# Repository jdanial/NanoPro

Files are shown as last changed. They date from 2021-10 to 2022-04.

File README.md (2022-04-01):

# NanoPro
## About
**NanoPro 1.0** is an affordable, high-quality, user-friendly, and do-it-yourself single-molecule microscope for super-resolution imaging.  
  
## Assembly and Operation
**NanoPro 1.0** assembly and operation is described in two parts. Part 1 describes assembly and validation of **NanoPro 1.0** and is published as follows:  

**Danial, JSH, Lam, JYL, Wu, Y, Woolley, M, Dimou, E, Cheetham, MR, Emin, D, and Klenerman, D.**  
Constructing a cost-efficient, high-throughput and high-quality single molecule localization microscope for super resolution imaging.  
_Nature Protocols_, 2022.  
  
Files referred to as supplementary in Part 1 can be found [here](https://github.com/jdanial/NanoPro/tree/main/Supplementary%20Files).
  
Part 2 describes the installation and operation of the **NanoPro 1.0** control software and can be found [here](https://github.com/jdanial/NanoPro/blob/main/Part%202%2C%20NanoPro%201.0%20Operation%20Manual.pdf).  
  
Updates (i.e. variations) to parts 1 and 2 are published at:  
https://github.com/jdanial/NanoPro  
  
## Use and citation
Any data or publications arising from the use of NanoPro 1.0 should cite the following paper:  
  
**Danial, JSH, Lam, JYL, Wu, Y, Woolley, M, Dimou, E, Cheetham, MR, Emin, D, and Klenerman, D.**  
Constructing a cost-efficient, high-throughput and high-quality single molecule localization microscope for super resolution imaging.  
_Nature Protocols_, 2022.

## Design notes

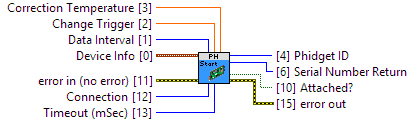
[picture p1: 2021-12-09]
Supplementary Files/Software/Source code/Dependencies/Phidgets/Phidget PH Sensor/Phidget PH Sensor Documentation/PHSensorStartc.png

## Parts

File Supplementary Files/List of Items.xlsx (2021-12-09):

Category | Item number | Description | Catalogue number | Vendor | Quantity | Price Per Item (USD, ex. VAT) | Line Price (USD, ex. VAT) | Order Link | Item Image
Fibre | 1 | 70 µm x 70 µm, NA=0.22, L=2m, FC/PC connector, square-core fibre cable | 05806-1 Rev. A | CeramOptec GmbH | 2 | 230.4 | 460.8 | https://www.ceramoptec.com/home.html | Not Available
Fibre | 2 | 40 mm focal length, FC/PC connector, achromatic fibre collimator | C40FC-A | Thorlabs | 1 | 926.6 | 926.6 | https://www.thorlabs.com/
Light | 3 | 561 nm, 100 mW laser | RLTMLL-561-100-3 | Roithner LaserTechnik | 1 | 4656 | 4656 | http://www.roithner-laser.com/ | Not Available
Light | 4 | 10 KHz, analog modulation unit | RLTMXL ANALOG 10KHZ | Roithner LaserTechnik | 1 | 789.3 | 789.3 | http://www.roithner-laser.com/ | Not Available
Light | 5 | 350 mW, 405nm diode laser with cooling option | PD-01254-E | Lasertack GmbH | 1 | 376.4 | 376.4 | https://www.lasertack.com/
Light | 6 | 55 mW, 488nm diode laser with cooling option | PD-01339-E | Lasertack GmbH | 1 | 431.1 | 431.1 | https://www.lasertack.com/
Light | 7 | 700 mW, 635nm diode laser with cooling option | PD-01229-E | Lasertack GmbH | 1 | 398.5 | 398.5 | https://www.lasertack.com/
Light | 8 | 20 mW, 850 nm compact diode laser module with shutter | LDM850 | Thorlabs | 1 | 736.1 | 736.1 | https://www.thorlabs.com/
Light | 9 | 740 mW, 4900 K, 1225 mA mounted LED | MNWHL4 | Thorlabs | 1 | 163.4 | 163.4 | https://www.thorlabs.com/
Light analysis | 10 | 320-1100 nm, 2D lateral effect position sensor | PDP90A | Thorlabs | 1 | 431.4 | 431.4 | https://www.thorlabs.com/
Light analysis | 11 | 700-1400 nm, IR detector card | VRC5 | Thorlabs | 1 | 140.1 | 140.1 | https://www.thorlabs.com/
Light analysis | 12 | Digital LCD, compact power and energy meter console | PM100D | Thorlabs | 1 | 1171 | 1171 | https://www.thorlabs.com/
Light analysis | 13 | 400-1100 nm, 500 mW, Standard Photodiode Power Sensor | S121C | Thorlabs | 1 | 362.3 | 362.3 | https://www.thorlabs.com/
Light analysis | 14 | Prime BSI Express, sCMOS camera | O1_PRIME_BSI_EXP | Teledyne Photometrics | 1 | 11645 | 11645 | https://www.photometrics.com/
Motion control | 15 | Enhanced blocking force and integrated sensor, 51 mm travel, positioner | SLC-1780-D-S | Smaract | 3 | 2258 | 6774 | https://www.smaract.com/index-en
Motion control | 16 | MSC2 sensor module | MCS2-S-0001 | Smaract | 1 | 646.6 | 646.6 | https://www.smaract.com/index-en | Not Available
Motion control | 17 | MSC2 control system | MCS2-C-0002 | Smaract | 1 | 2073.8 | 2073.8 | https://www.smaract.com/index-en
Motion control | 18 | K-Cube PSD auto aligner | KPA101 | Thorlabs | 1 | 877.3 | 877.3 | https://www.thorlabs.com/
Optics | 19 | Apochromatic, 100x magnification, 1.49 numerical aperture, TIRF objective | MRD01991 | Nikon | 1 | 8487.2 | 8487.2 | https://www.nikon.com/
Optics | 20 | 405/488/561/635/800-1050 nm, BrightLine® multiphoton super resolution dichroic splitter | DI01-R405/488/561/635/800-T1-25X36 | Semrock | 1 | 1039 | 1039 | https://www.semrock.com/
Optics | 21 | 390/482/564/640 nm, BrightLine® quad-band bandpass filter | FF01-390/482/563/640-25 | Semrock | 1 | 743.9 | 743.9 | https://www.semrock.com/
Optics | 22 | 446/523/600/677 nm, BrightLine® quad-band bandpass filter | FF01-446/523/600/677-25 | Semrock | 1 | 691.3 | 691.3 | https://www.semrock.com/
Optics | 23 | 525/30 nm, BrightLine® single-band bandpass filter | FF01-525/30-25 | Semrock | 1 | 431.6 | 431.6 | https://www.semrock.com/
Optics | 24 | 600/37 nm, BrightLine® single-band bandpass filter | FF01-600/37-25 | Semrock | 1 | 401.1 | 401.1 | https://www.semrock.com/
Optics | 25 | 676/29 nm, BrightLine® single-band bandpass filter | FF01-676/29-25 | Semrock | 1 | 431.6 | 431.6 | https://www.semrock.com/
Optics | 26 | 700 nm, BrightLine® multiphoton short pass dichroic beam splitter | FF700-SDI01-25X36 | Semrock | 1 | 743.9 | 743.9 | https://www.semrock.com/
Optics | 27 | 425 nm, long pass dichroic mirror | DMLP425 | Thorlabs | 1 | 137.2 | 137.2 | https://www.thorlabs.com/
Optics | 28 | 505 nm, long pass dichroic mirror | DMLP505 | Thorlabs | 1 | 137.2 | 137.2 | https://www.thorlabs.com/
Optics | 29 | 605 nm, long pass dichroic mirror | DMLP605 | Thorlabs | 1 | 137.2 | 137.2 | https://www.thorlabs.com/
Optics | 30 | 805 nm, long pass dichroic mirror | DMLP805 | Thorlabs | 1 | 211.8 | 211.8 | https://www.thorlabs.com/
Optics | 31 | 700 nm, premium long pass filter | FELH0700 | Thorlabs | 1 | 134.5 | 134.5 | https://www.thorlabs.com/
Optics | 32 | 400-750 nm, broadband dielectric mirror | BB1-E02 | Thorlabs | 10 | 79.5 | 795 | https://www.thorlabs.com/
Optics | 33 | 750-1100 nm, broadband dielectric mirror | BB1-E03 | Thorlabs | 1 | 79.5 | 79.5 | https://www.thorlabs.com/
Optics | 34 | 125 mm focal length, achromatic doublet | AC254-125-A-ML | Thorlabs | 1 | 79.5 | 79.5 | https://www.thorlabs.com/
Optics | 35 | 200 mm focal length, tube lens | TTL200-A | Thorlabs | 1 | 510.4 | 510.4 | https://www.thorlabs.com/
Optics | 36 | 11 mm focal length, 0.25 numerical aperture, aspheric lens | C220TMD-A | Thorlabs | 1 | 78.86 | 78.86 | https://www.thorlabs.com/
Optics | 37 | 1.0 optical density, neutral density filter | NE10B-A | Thorlabs | 1 | 62 | 62 | https://www.thorlabs.com/
Optics | 38 | 700-1100 nm, 30 mm, non-polarising beam splitter | CCM1-BS014/M | Thorlabs | 1 | 315.8 | 315.8 | https://www.thorlabs.com/
Optics | 39 | Variable line grating test target | R1L3S6P | Thorlabs | 1 | 510.4 | 510.4 | https://www.thorlabs.com/
Optics | 40 | Pack of 1000, 26x76 mm, #1.5 Menzel Glaser glass coverslips | MENZBC026076AC40 | VWR | 1 | 92.5 | 92.5 | https://www.vwr.com/
Optoelectronics | 41 | Intel® Core™ i9 processor, NVIDIA® GeForce® GTX 1650 Ti 4GB, 32 GB RAM, 1 TB SSD, laptop | XPS 15 (9500) | Dell | 1 | 3002 | 3002 | https://www.dell.com/en-uk
Optoelectronics | 42 | 7-port, USB 3.0 hub | 138-5514 | RS Components | 1 | 104.6 | 104.6 | https://uk.rs-online.com/web/
Optoelectronics | 43 | Sony PlayStation DualShock 4 controller | CS30605 | Onecall | 1 | 61.6 | 61.6 | https://onecall.farnell.com/
Optoelectronics | 44 | 4-output, digital analog converter device | 1002_0B | Active Robots Ltd. | 1 | 113.2 | 113.2 | https://www.active-robots.com/
Optoelectronics | 45 | 6-output, control hub | HUB0000_0 | Active Robots Ltd. | 1 | 39.9 | 39.9 | https://www.active-robots.com/
Optoelectronics | 46 | 5 V, constant DC power source device | PSU2000_0 | Active Robots Ltd. | 1 | 16 | 16 | https://www.active-robots.com/
Optoelectronics | 47 | 1.5 V-5 V, variable DC power source device | PSU2001_0 | Active Robots Ltd. | 1 | 19.2 | 19.2 | https://www.active-robots.com/
Optoelectronics | 48 | 60 cm, mini-USB cable | 3036_0 | Active Robots Ltd. | 2 | 5.6 | 11.2 | https://www.active-robots.com/
Optoelectronics | 49 | 60 cm, converter device cable | 3002_0 | Active Robots Ltd. | 2 | 3.2 | 6.4 | https://www.active-robots.com/
Optoelectronics | 50 | 12 outlet, surge-protected power strip | HDPS12-UK [for UK], HDPS12-US [for US], HDPS12-EU [for EU] | Thorlabs | 1 | 66.2 | 66.2 | https://www.thorlabs.com/
Optoelectronics | 51 | 1 m, black cable trunking | CMS002 | Thorlabs | 1 | 26.6 | 26.6 | https://www.thorlabs.com/
Optoelectronics | 52 | 15 V, 2.4 A power supply unit for one K- or T-cube | KPS101 | Thorlabs | 1 | 36.3 | 36.3 | https://www.thorlabs.com/
Optoelectronics | 53 | 15 V/5 V, power supply unit for K- or T-cubes | TPS002 | Thorlabs | 1 | 120.1 | 120.1 | https://www.thorlabs.com/
Optoelectronics | 54 | T-cube LED driver | LEDD1B | Thorlabs | 1 | 332.2 | 332.2 | https://www.thorlabs.com/
Optoelectronics | 55 | 914 mm, male to male, BNC coaxial cable | 2249-C-36 | Thorlabs | 2 | 18.55 | 37.1 | https://www.thorlabs.com/
Optoelectronics | 56 | BNC to test clips | T3788 | Thorlabs | 2 | 13.5 | 27 | https://www.thorlabs.com/
Optoelectronics | 57 | 12 V, 80 W, 100-240 VAC, power supply for laser modules | PD-01341-E | Lasertack GmbH | 3 | 50.3 | 150.9 | https://www.lasertack.com/
Optoelectronics | 58 | 30 A, 250 V, terminal strip | 782-2857 | RS Components | 1 | 2 | 2 | https://uk.rs-online.com/web/
Optoelectronics | 59 | 10 m, unscreened flat ribbon cable | 214-0683 | RS Components | 1 | 38.7 | 38.7 | https://uk.rs-online.com/web/
Optoelectronics | 60 | 1 m, IEC power cable | 731-6185 [for UK], 731-6163 [for US], 626-6751 [for EU] | RS Components | 3 | 17.8 | 53.4 | https://uk.rs-online.com/web/
Optoelectronics | 61 | 5 mm, vibration motor | 304-116 | Precision Microdrives Ltd | 5 | 6.5 | 32.5 | https://www.precisionmicrodrives.com/
Optoelectronics | 62 | 1.2 m, Micro B to USB A 2.0 cable | 876-2403 | RS Components | 1 | 6.4 | 6.4 | https://uk.rs-online.com/web/
Optomechanics | 63 | 700 mm x 900 mm x 1500 mm, heavy-duty passive frame | PFH90150-8 | Thorlabs | 1 | 2132.6 | 2132.6 | https://www.thorlabs.com/
Optomechanics | 64 | 110 mm x 900 mm x 1500 mm, breadboard | B90150B | Thorlabs | 1 | 2475 | 2475 | https://www.thorlabs.com/
Optomechanics | 65 | Passive isolation foot pump | PTA127 | Thorlabs | 1 | 51.2 | 51.2 | https://www.thorlabs.com/
Optomechanics | 66 | Fibre launch system | KT120/M | Thorlabs | 1 | 1216.9 | 1216.9 | https://www.thorlabs.com/
Optomechanics | 67 | Four-position slider bundle | ELL9K | Thorlabs | 1 | 375 | 375 | https://www.thorlabs.com/
Optomechanics | 68 | 225 mm, square construction rail | XE25L225/M | Thorlabs | 4 | 16.7 | 66.8 | https://www.thorlabs.com/
Optomechanics | 69 | 50 mm length, 25 mm diameter, pedestal pillar post | RS2P/M | Thorlabs | 12 | 29.7 | 356.4 | https://www.thorlabs.com/
Optomechanics | 70 | 38 mm length, 25 mm diameter, pedestal pillar post | RS1.5P/M | Thorlabs | 4 | 27 | 108 | https://www.thorlabs.com/
Optomechanics | 71 | 2 in length, 1 in diameter, pedestal pillar post | RS2P | Thorlabs | 1 | 29.7 | 29.7 | https://www.thorlabs.com/
Optomechanics | 72 | Pack of 5, 50 mm length, 12.7 mm diameter, optical post | TR50/M-P5 | Thorlabs | 2 | 24.7 | 49.4 | https://www.thorlabs.com/
Optomechanics | 73 | Pack of 5, 30 mm length, 12.7 mm diameter, optical post | TR30/M-P5 | Thorlabs | 1 | 22.6 | 22.6 | https://www.thorlabs.com/
Optomechanics | 74 | Pack of 5, 50 mm length, 12.7 mm diameter, post holder | PH50/M-P5 | Thorlabs | 3 | 40.8 | 122.4 | https://www.thorlabs.com/
Optomechanics | 75 | 1.24 in slot length, clamping fork | CF125 | Thorlabs | 1 | 9.5 | 9.5 | https://www.thorlabs.com/
Optomechanics | 76 | Pack of 4, 0.5 in length, 6 mm diameter, cage assembly rod | ER05-P4 | Thorlabs | 9 | 20.3 | 182.7 | https://www.thorlabs.com/
Optomechanics | 77 | 0.25 in length, 6 mm diameter, cage assembly rod | ER025 | Thorlabs | 8 | 5.3 | 42.4 | https://www.thorlabs.com/
Optomechanics | 78 | Pack of 4, 6 mm diameter, rod adaptor | ERSCB-P4 | Thorlabs | 2 | 61.7 | 123.4 | https://www.thorlabs.com/
Optomechanics | 79 | Kinematic mirror mount | KM100CP/M | Thorlabs | 4 | 78.4 | 313.6 | https://www.thorlabs.com/
Optomechanics | 80 | 30 mm, right-angle kinematic mirror mount | KCB1C/M | Thorlabs | 3 | 151.3 | 453.9 | https://www.thorlabs.com/
Optomechanics | 81 | 30 mm, cage cube with dichroic filter mount | CM1-DCH/M | Thorlabs | 3 | 180.1 | 540.3 | https://www.thorlabs.com/
Optomechanics | 82 | 30 mm, 0.5 in thickness, cage plate | CP33T/M | Thorlabs | 3 | 23.9 | 71.7 | https://www.thorlabs.com/
Optomechanics | 83 | Compact kinematic mirror mount | KMS/M | Thorlabs | 8 | 41.1 | 328.8 | https://www.thorlabs.com/
Optomechanics | 84 | 1 in diameter, 2.5-6.1 mm thickness, mirror holder | MH25 | Thorlabs | 8 | 16.3 | 130.4 | https://www.thorlabs.com/
Optomechanics | 85 | Rotation mount for 1 in optics | LRM1 | Thorlabs | 3 | 95.9 | 287.7 | https://www.thorlabs.com/
Optomechanics | 86 | 2 in travel, SM1 zoom housing | SM1NR1 | Thorlabs | 1 | 221.3 | 221.3 | https://www.thorlabs.com/
Optomechanics | 87 | SM1 end cap | SM1CP2 | Thorlabs | 3 | 19.34 | 58.02 | https://www.thorlabs.com/
Optomechanics | 88 | SM1 coupler | SM1T2 | Thorlabs | 2 | 22.1 | 44.2 | https://www.thorlabs.com/
Optomechanics | 89 | Adaptor with external SM1 threads and internal SM2 threads | SM1A2 | Thorlabs | 2 | 27.2 | 54.4 | https://www.thorlabs.com/
Optomechanics | 90 | Adaptor with external SM1 threads and internal M25 x 0.75 threads | SM1A12 | Thorlabs | 1 | 22.5 | 22.5 | https://www.thorlabs.com/
Optomechanics | 91 | Adaptor with external SM05 threads and internal SM1 threads | SM1A1 | Thorlabs | 1 | 22.5 | 22.5 | https://www.thorlabs.com/
Optomechanics | 92 | Adaptor with external C-mount threads and external SM1 threads | SM1A39 | Thorlabs | 1 | 21.8 | 21.8 | https://www.thorlabs.com/
Optomechanics | 93 | 4 in, SM1 lens tube | SM1L40 | Thorlabs | 1 | 48.6 | 48.6 | https://www.thorlabs.com/
Optomechanics | 94 | Pack of 5, 0.3 in, SM1 lens tube | SM1L03-P5 | Thorlabs | 1 | 61.1 | 61.1 | https://www.thorlabs.com/
Optomechanics | 95 | 0.5 in, SM1 lens tube without external threads | SM1M05 | Thorlabs | 1 | 13.7 | 13.7 | https://www.thorlabs.com/
Optomechanics | 96 | 1 in, SM1 lens tube spacer | SM1S10 | Thorlabs | 1 | 13.7 | 13.7 | https://www.thorlabs.com/
Optomechanics | 97 | FC/PC fibre adaptor cap with internal SM1 threads | S120-FC | Thorlabs | 1 | 43.4 | 43.4 | https://www.thorlabs.com/
Optomechanics | 98 | SM1 thread spanner wrench | SPW602 | Thorlabs | 1 | 29.2 | 29.2 | https://www.thorlabs.com/
Optomechanics | 99 | 9-piece hex key set | CCHK/M | Thorlabs | 1 | 25.6 | 25.6 | https://www.thorlabs.com/
Optomechanics | 100 | 4-40 cap screw and hardware kit | HW-KIT5 | Thorlabs | 1 | 107.9 | 107.9 | https://www.thorlabs.com/
Optomechanics | 101 | M6 cap screw and hardware kit | HW-KIT2/M | Thorlabs | 1 | 124.5 | 124.5 | https://www.thorlabs.com/
Optomechanics | 102 | Pack of 25, 0.25"-20 in thread, 0.5 in length, stainless steel setscrew | SS25S050 | Thorlabs | 1 | 6.3 | 6.3 | https://www.thorlabs.com/
Optomechanics | 103 | Pack of 2, microscope slide spring clips | SLH1/M | Thorlabs | 1 | 47 | 47 | https://www.thorlabs.com/
Optomechanics | 104 | Bullseye level | LVL01 | Thorlabs | 1 | 4.1 | 4.1 | https://www.thorlabs.com/
Optomechanics | 105 | Pack of 2, handles | BBH1 | Thorlabs | 1 | 15.8 | 15.8 | https://www.thorlabs.com/
Optomechanics | 106 | Hinge for rail enclosures | XE25H | Thorlabs | 2 | 11.3 | 22.6 | https://www.thorlabs.com/
Optomechanics | 107 | Lid stop for rail enclosures | XE25LS | Thorlabs | 1 | 7.9 | 7.9 | https://www.thorlabs.com/
Optomechanics | 108 | 20 mm x 235 mm x 275 mm, 5080 aluminium tool plate | 277120 | Aalco | 2 | 28.1 | 56.2 | https://www.aalco.co.uk/ | Not Available
Optomechanics | 109 | 20 mm x 160 mm x 235 mm, 5080 aluminium tool plate | 277121 | Aalco | 2 | 17.1 | 34.2 | https://www.aalco.co.uk/ | Not Available
Optomechanics | 110 | 20 mm x 200 mm x 275 mm, 5080 aluminium tool plate | 277122 | Aalco | 2 | 24.7 | 49.4 | https://www.aalco.co.uk/ | Not Available
Optomechanics | 111 | 20 mm x 105 mm x 130 mm, 5080 aluminium tool plate | 277124 | Aalco | 3 | 9.6 | 28.8 | https://www.aalco.co.uk/ | Not Available
Optomechanics | 112 | 20 mm x 105 mm x 230 mm, 5080 aluminium tool plate | 277125 | Aalco | 1 | 12.3 | 12.3 | https://www.aalco.co.uk/ | Not Available
Optomechanics | 113 | 20 mm x 80 mm x 90 mm, 5080 aluminium tool plate | 277129 | Aalco | 1 | 9.6 | 9.6 | https://www.aalco.co.uk/ | Not Available
Optomechanics | 114 | 20 mm x 45 mm x 105 mm, 5080 aluminium tool plate | 277131 | Aalco | 1 | 9.6 | 9.6 | https://www.aalco.co.uk/ | Not Available
Optomechanics | 115 | Wire stripper | 663-617 | RS Components | 1 | 41.3 | 41.3 | https://uk.rs-online.com/web/
Optomechanics | 116 | Pack of 15, 32 mm length, 6 mm diameter plain steel dowel pin | 270-653 | RS Components | 1 | 6.6 | 6.6 | https://uk.rs-online.com/web/
Optomechanics | 117 | Pack of 20, 24 mm length, 4 mm diameter plain steel dowel pin | 270-596 | RS Components | 1 | 7.6 | 7.6 | https://uk.rs-online.com/web/
Optomechanics | 118 | Pack of 100, 20 mm length, M1.6, TORX®, stainless steel screw | 179-5712 | RS Components | 1 | 51.9 | 51.9 | https://uk.rs-online.com/web/
Optomechanics | 119 | Pack of 10, 15 mm x 15 mm, steel angle bracket | 427-991 | RS Components | 1 | 0.3 | 0.3 | https://uk.rs-online.com/web/
Optomechanics | 120 | Pack of 250, 0.3 mm thickness, M1.6, stainless steel plain washer | 179-5724 | RS Components | 1 | 4.1 | 4.1 | https://uk.rs-online.com/web/
Optomechanics | 121 | Pack of 10, M6, clamping knob | 830-4158 | RS Components | 1 | 1.6 | 1.6 | https://uk.rs-online.com/web/
Optomechanics | 122 | Planar connecting element | SCE-CN | Smaract | 1 | 268.5 | 268.5 | https://www.smaract.com/index-en | Not Available
Optomechanics | 123 | Rectangular connecting element | SCE-RN | Smaract | 1 | 549.2 | 549.2 | https://www.smaract.com/index-en | Not Available
Optomechanics | 124 | TORX® T5, screwdriver | 4432850 | Farnell | 1 | 6 | 6 | https://uk.farnell.com/
Optomechanics | 125 | 2.5 mm x 50 mm, slotted, screwdriver | 3378478 | Farnell | 1 | 7.6 | 7.6 | https://uk.farnell.com/
Optomechanics | 126 | 525 pieces, M3 to M6, socket cap screw kit | TRFAKIT0005 | Onecall | 1 | 81.5 | 81.5 | https://onecall.farnell.com/
Optomechanics | 127 | 2440 mm x 1220 mm x 5 mm, black foam PVC | None | Vision Plastics Ltd | 1 | 56.6 | 56.6 | https://visionplastics.co.uk/
Optomechanics | 128 | 1000 mm x 1000 mm x 8mm, clear Perspex | None | Engineering & Design Plastics Ltd | 1 |  | 0 | https://www.edplastics.co.uk/
Optomechanics | 129 | Laser plates | None | Custom fabrication | 1 | 400 | 400 | Not Available | Not Available
Optomechanics | 130 | Laser combiner enclosure | None | Custom fabrication | 1 | 100 | 100 | Not Available | Not Available
Optomechanics | 131 | Positioner base | None | Custom fabrication | 1 | 100 | 100 | Not Available | Not Available
Optomechanics | 132 | Microscope box | None | Custom fabrication | 1 | 600 | 600 | Not Available | Not Available
Optomechanics | 133 | Sample enclosure | None | Custom fabrication | 1 | 600 | 600 | Not Available | Not Available
Optomechanics | 134 | Sample holder | None | Custom fabrication | 1 | 100 | 100 | Not Available | Not Available
Sample | 135 | 40 nm, Cy3B, immobilized high-resolution DNA-PAINT nanorulers | 3030 | GATTAquant | 1 | 409.7 | 409.7 | https://www.gattaquant.com/ | Not Available
Sample | 136 | 20 nm, Cy3B, immobilized high-resolution DNA-PAINT nanorulers | 3031 | GATTAquant | 1 | 409.7 | 409.7 | https://www.gattaquant.com/ | Not Available
Safety | 137 | 12% visible light transmission, universal style, laser safety glasses | LG4 | Thorlabs | 1 | 182.3 | 182.3 | https://www.thorlabs.com/
Software | 138 | Supplementary software | None | None | 1 | 0 | 0 | Not Available | Not Available
Software | 139 | ImageJ software (https://imagej.nih.gov/ij/) | None | None | 1 | 0 | 0 | https://imagej.nih.gov/ij/ | Not Available
Other | 140 | Low autofluorescence immersion oil | MOIL-30 | Thorlabs | 1 | 75.9 | 75.9 | https://www.thorlabs.com/
Other | 141 | Fibre and vibration motor mount | None | Custom fabrication | 1 | 10 | 10 | Not Available | Not Available
Other | 142 | Lens cleaning tissue | WHA2105862 | Merck | 1 | 55.7 | 55.7 | https://www.merck.com/
Other | 143 | Park of 25, thick Viton O Ring | OR26X2V175 | Hooper Ltd. | 1 | 35.3 | 35.3 | http://www.hooperlimited.co.uk/ | Not Available
Other | 144 | Pack of 50, thin Viton O Ring | OR26X1V175 | Hooper Ltd. | 1 | 12.2 | 12.2 | http://www.hooperlimited.co.uk/ | Not Available
Other | 145 | 25.1 mm focal length, Plano convex lens | LA1951-ML | Thorlabs | 1 | 38.8 | 38.8 | https://www.thorlabs.com/
Other | 146 | 1 in, SM1 lens tube | SM1L10 | Thorlabs | 1 | 14.53 | 14.53 | https://www.thorlabs.com/
Total Price (USD) |  |  |  |  |  |  | 68548.21
Total Price (GBP) |  |  |  |  |  |  | 50040.1933
Total Price (EUR) |  |  |  |  |  |  | 58951.4606

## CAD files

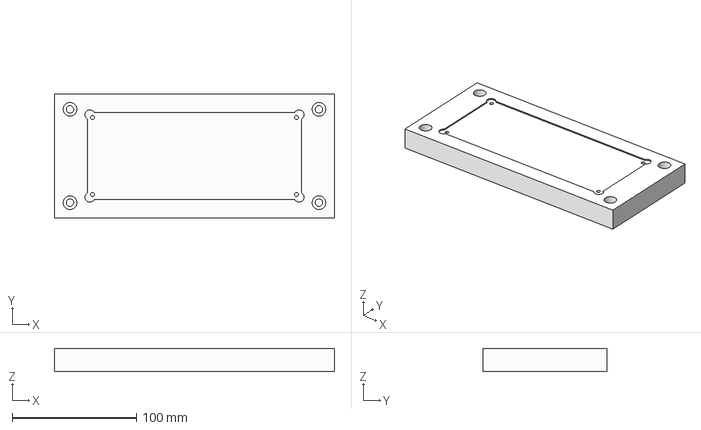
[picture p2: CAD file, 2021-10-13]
Supplementary Files/CAD files/CAD_File 2.step
225.0 x 100.0 x 18.7 mm

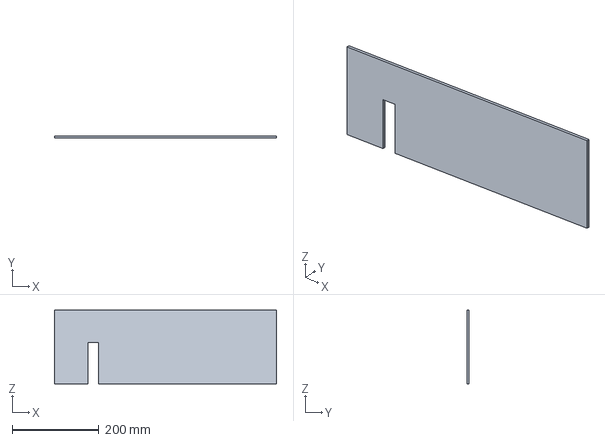
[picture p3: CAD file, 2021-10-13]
Supplementary Files/CAD files/CAD_File 23.step
512.0 x 5.20 x 170.0 mm

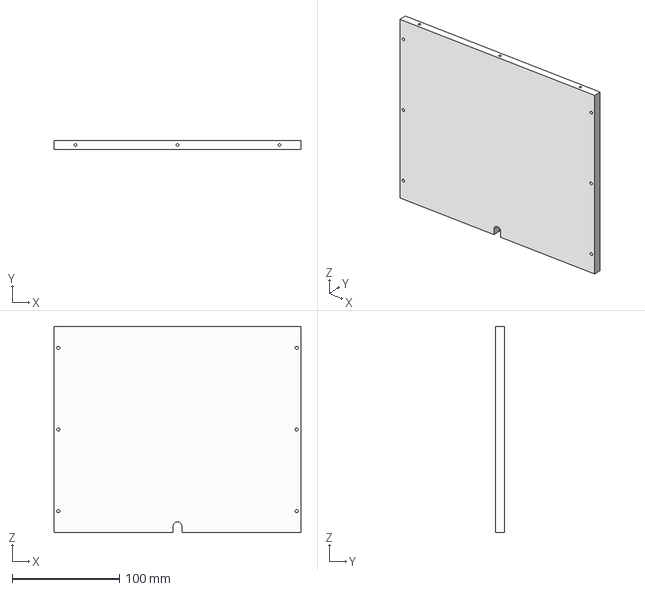
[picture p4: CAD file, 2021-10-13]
Supplementary Files/CAD files/CAD_File 11.step
230.0 x 8.00 x 192.0 mm

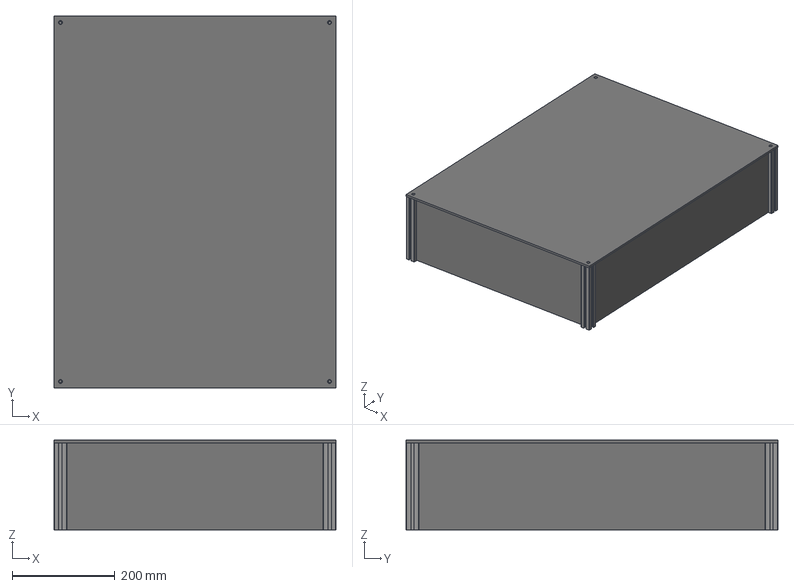
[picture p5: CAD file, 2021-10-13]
Supplementary Files/CAD files/CAD_File 20.step
550.0 x 725.0 x 175.2 mm
Construction rails
Lid
Side Panel 1

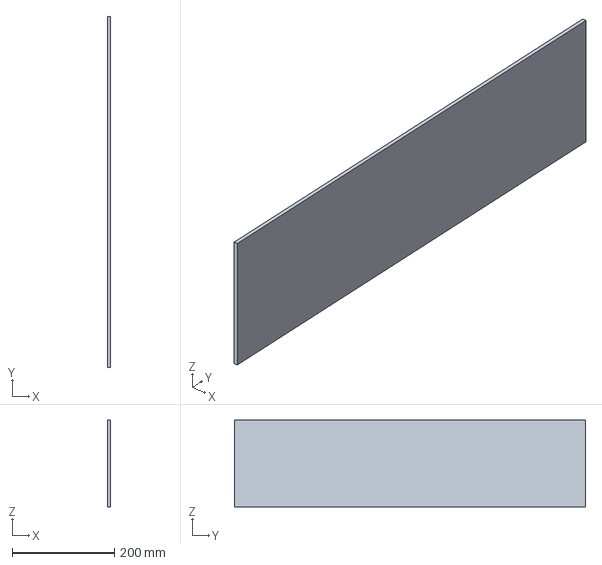
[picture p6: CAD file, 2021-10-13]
Supplementary Files/CAD files/CAD_File 25.step
5.20 x 687.0 x 170.0 mm

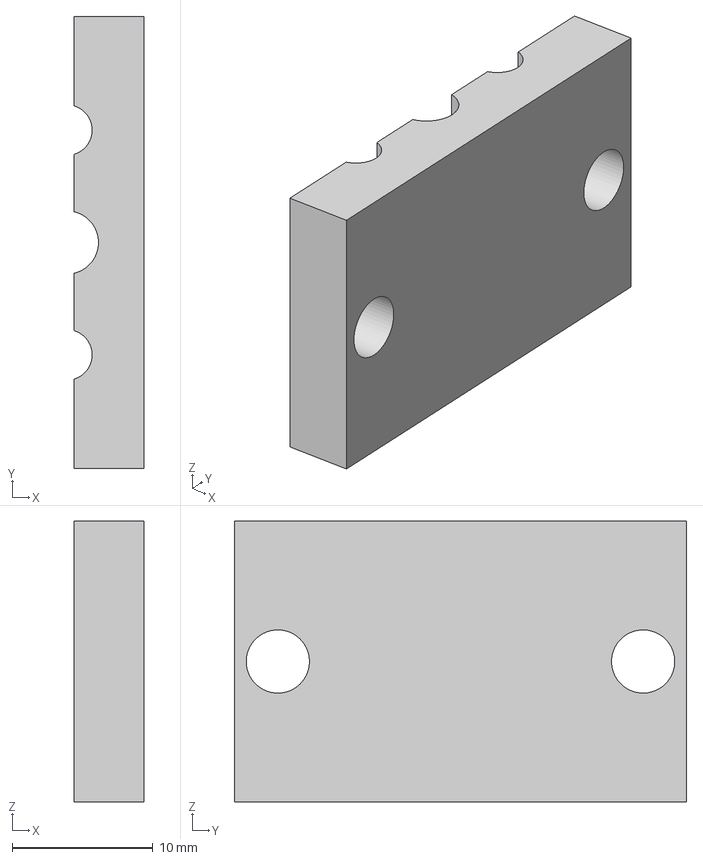
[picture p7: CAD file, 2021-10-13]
Supplementary Files/CAD files/CAD_File 18.step
5.00 x 32.2 x 20.0 mm

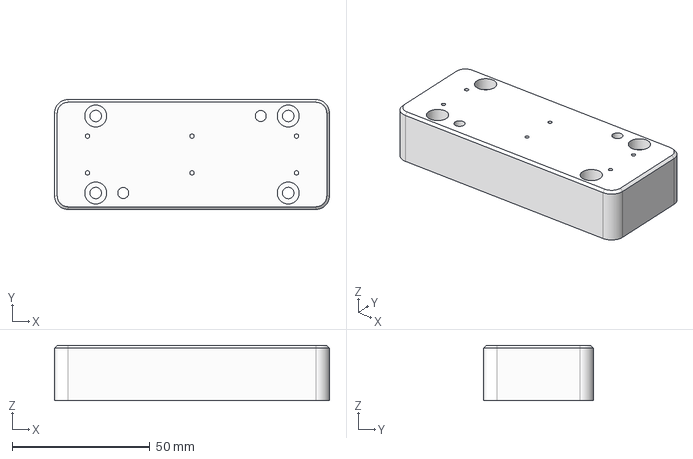
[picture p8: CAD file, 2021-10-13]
Supplementary Files/CAD files/CAD_File 4.step
100.0 x 40.0 x 20.0 mm

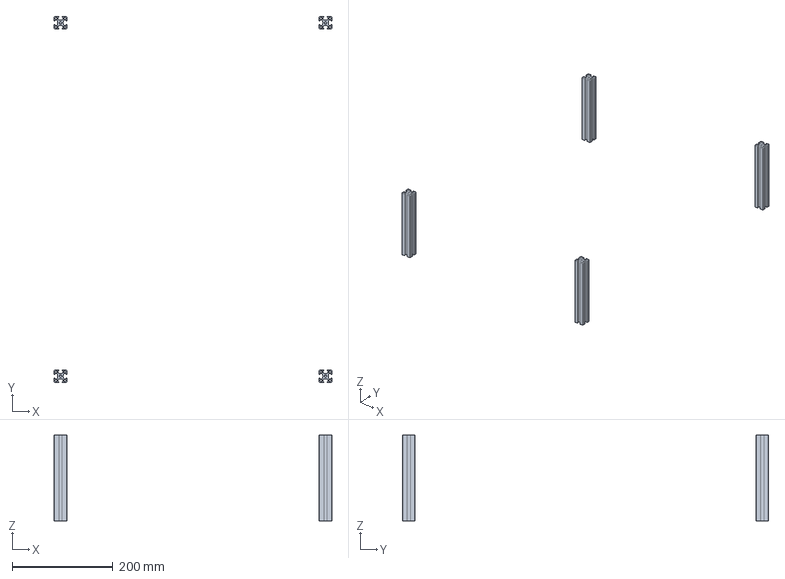
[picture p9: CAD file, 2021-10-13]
Supplementary Files/CAD files/CAD_File 21.step
550.0 x 725.0 x 170.0 mm

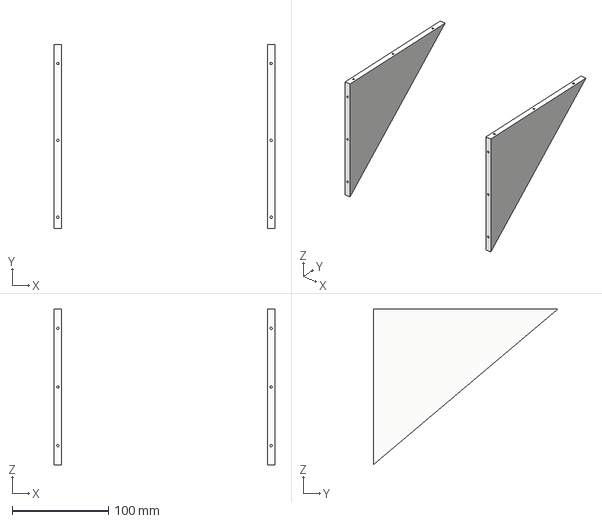
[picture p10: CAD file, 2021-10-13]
Supplementary Files/CAD files/CAD_File 17.step
230.0 x 192.0 x 162.0 mm

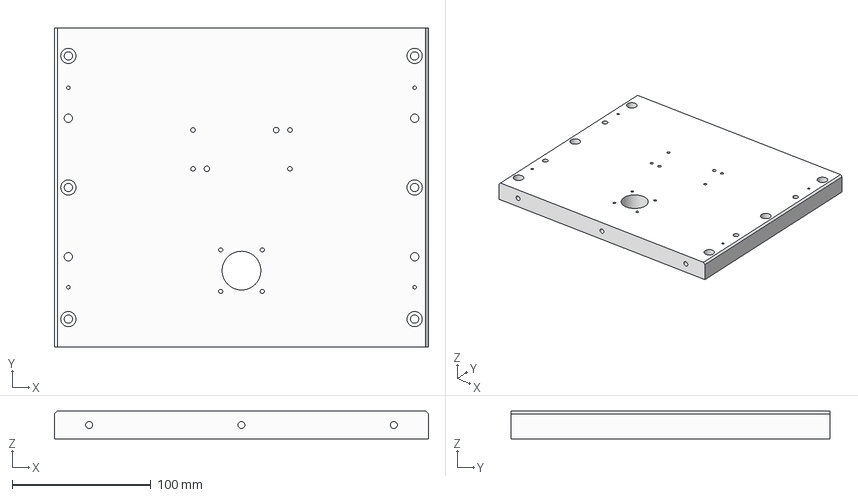
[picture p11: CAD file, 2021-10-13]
Supplementary Files/CAD files/CAD_File 5.step
270.0 x 230.0 x 20.0 mm

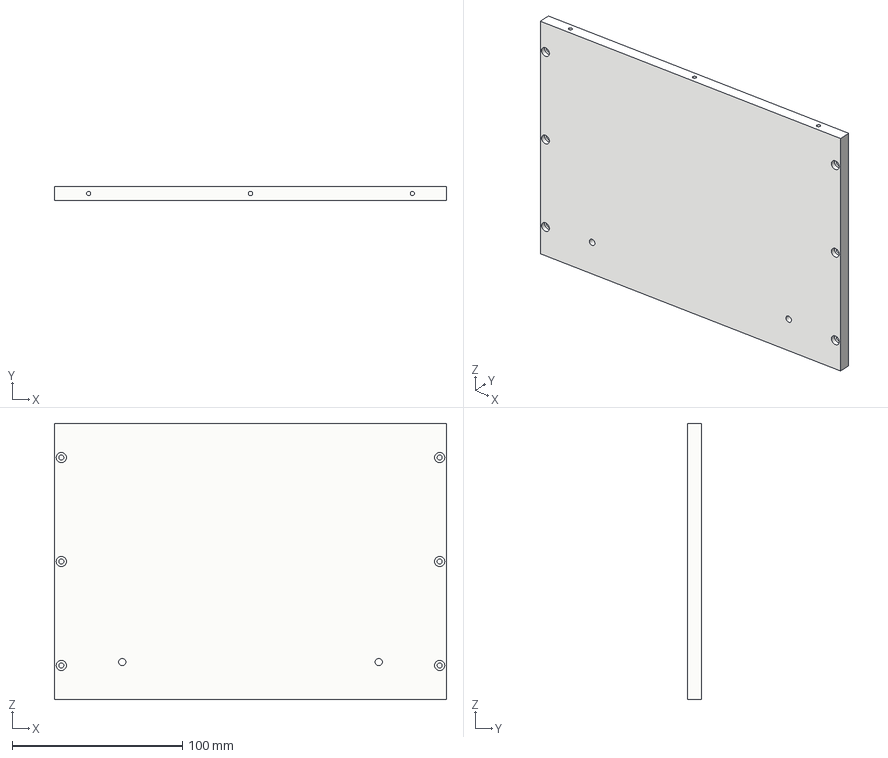
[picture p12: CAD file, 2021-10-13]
Supplementary Files/CAD files/CAD_File 16.step
230.0 x 8.00 x 162.0 mm

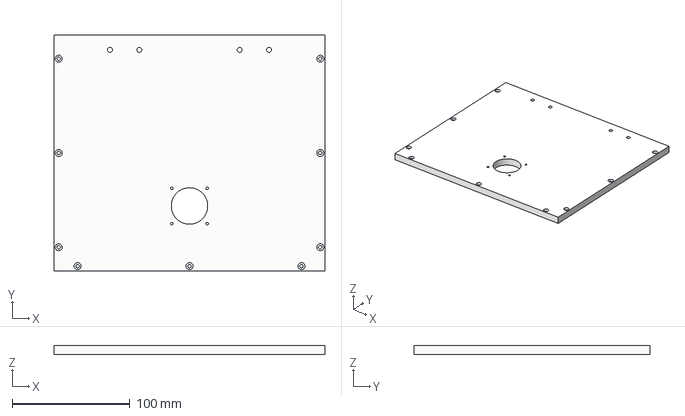
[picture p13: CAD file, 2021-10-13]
Supplementary Files/CAD files/CAD_File 15.step
230.0 x 199.9 x 8.00 mm

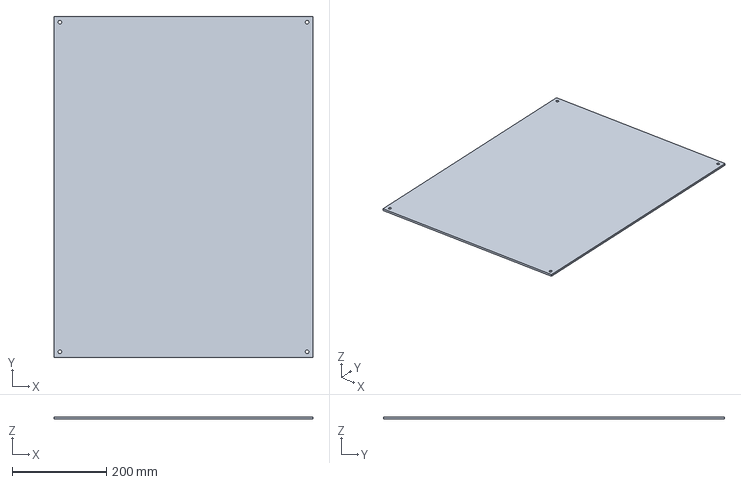
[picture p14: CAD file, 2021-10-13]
Supplementary Files/CAD files/CAD_File 22.step
550.0 x 725.0 x 5.20 mm

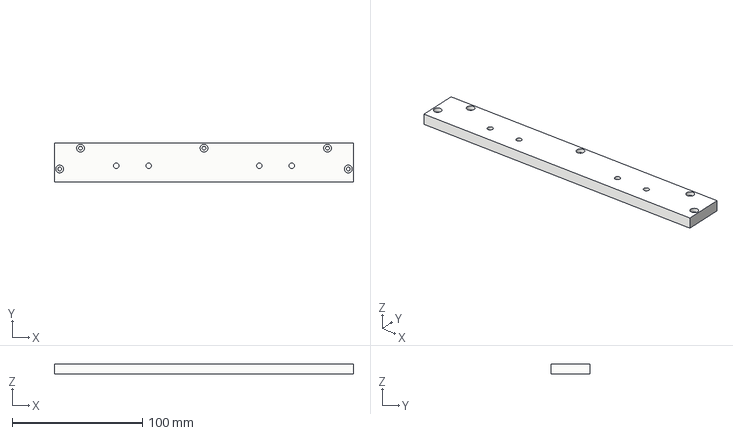
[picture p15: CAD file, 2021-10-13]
Supplementary Files/CAD files/CAD_File 13.step
230.0 x 30.0 x 8.00 mm

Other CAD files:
Supplementary Files/CAD files/CAD_File 24.step
Supplementary Files/CAD files/CAD_File 26.step
Supplementary Files/CAD files/CAD_File 6.step
Supplementary Files/CAD files/CAD_File 3.step
Supplementary Files/CAD files/CAD_File 1.f3d
Supplementary Files/CAD files/CAD_File 1.step
Supplementary Files/CAD files/CAD_File 10.f3d
Supplementary Files/CAD files/CAD_File 10.step
Supplementary Files/CAD files/CAD_File 11.f3d
Supplementary Files/CAD files/CAD_File 12.f3d
Supplementary Files/CAD files/CAD_File 12.step
Supplementary Files/CAD files/CAD_File 13.f3d
Supplementary Files/CAD files/CAD_File 14.f3d
Supplementary Files/CAD files/CAD_File 14.step
Supplementary Files/CAD files/CAD_File 15.f3d
Supplementary Files/CAD files/CAD_File 16.f3d
Supplementary Files/CAD files/CAD_File 17.f3d
Supplementary Files/CAD files/CAD_File 18.f3d
Supplementary Files/CAD files/CAD_File 2.f3d
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

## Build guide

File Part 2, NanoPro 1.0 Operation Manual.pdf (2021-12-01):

NanoPro 1.0
Part 2: Installation and Operation Manual
Section | Page
Introduction | 2
License | 3
Use | 4
Hardware requirements | 5
Installation | 6
Software window | 8
Joystick functions | 9
Operation | Live imaging | 10
| Stage movement | 10
| Position recording | 10
| Auto focusing | 10
| Light source modulation | 10
| Single acquisition | 11
| Multi sample acquisition | 11
| Switching off software | 13

Updated 01.12.2021

Section 1: Introduction

NanoPro 1.0 is an affordable, high-quality, user-friendly, and do-it-yourself single-molecule microscope for super-resolution imaging.

NanoPro 1.0 assembly and operation is described in two parts. Part 1 describes assembly and validation and is published here:

Danial, JSH, Lam, JYL, Wu, Y, Woolley, M, Dimou, E, Cheetham, MR, Emin, D, and Klenerman, D.
Constructing a cost-efficient, high-throughput and high-quality single molecule localization microscope for super resolution imaging.
Nature Protocols, 2021.

This is Part 2 of the NanoPro 1.0 assembly and operation describing installation and operation of the control software.

Updates (i.e. variations) to parts 1 and 2 are published at:
https://github.com/jdanial/NanoPro

Section 2: License

MIT License

Copyright (c) 2021 Danial, JSH; Lam, JYL; Wu, Y; Woolley, M; Dimou, E; Cheetham, MR; Emin, D; and Klenerman, D.

Permission is hereby granted, free of charge, to any person obtaining a copy of this software and associated documentation files (NanoPro 1.0), to deal in the Software without restriction, including without limitation the rights to use, copy, modify, merge, publish, distribute, sublicense, and/or sell copies of the Software, and to permit persons to whom the Software is furnished to do so, subject to the following conditions:

The above copyright notice and this permission notice shall be included in all copies or substantial portions of the Software.

THE SOFTWARE IS PROVIDED "AS IS", WITHOUT WARRANTY OF ANY KIND, EXPRESS OR IMPLIED, INCLUDING BUT NOT LIMITED TO THE WARRANTIES OF MERCHANTABILITY, FITNESS FOR A PARTICULAR PURPOSE AND NONINFRINGEMENT. IN NO EVENT SHALL THE AUTHORS OR COPYRIGHT HOLDERS BE LIABLE FOR ANY CLAIM, DAMAGES OR OTHER LIABILITY, WHETHER IN AN ACTION OF CONTRACT, TORT OR OTHERWISE, ARISING FROM, OUT OF OR IN CONNECTION WITH THE SOFTWARE OR THE USE OR OTHER DEALINGS IN THE SOFTWARE.

Section 3: Use

The NanoPro 1.0 software can only be used to control the microscope described in:

Danial, JSH; Lam, JYL; Wu, Y; Woolley, M; Dimou, E; Cheetham, MR; Emin, D; and Klenerman, D.
Constructing a cost-efficient, high-throughput and high-quality single molecule localization microscope for super resolution imaging.
Nature Protocols, 2021.

Or any variations thereof described in:

https://github.com/jdanial/NanoPro

Any data or publications arising from the use of NanoPro 1.0 should cite the following paper:

Danial, JSH; Lam, JYL; Wu, Y; Woolley, M; Dimou, E; Cheetham, MR; Emin, D; and Klenerman, D.
Constructing a cost-efficient, high-throughput and high-quality single molecule localization microscope for super resolution imaging.
Nature Protocols, 2021.

Section 4: Hardware requirements

All hardware (mechanical, optical and electronic) that can be used with the NanoPro 1.0 software is described in:

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

Or any variations thereof described in:

https://github.com/jdanial/NanoPro

Section 5: Installation

Note:
Where Part 1 is referred to hereafter, see:

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

Or any variations thereof described in:

https://github.com/jdanial/NanoPro

1. Download and install the National Instruments LabVIEW 2020 SP1 64-bit runtime engine from the following link (https://www.ni.com/en-gb/support/downloads/software-products/download.labview.html#369642). (https://www.ni.com/en-gb/support/downloads/software-products/download.labview.html#369642)
2. Download and install the National Instruments VISA 20.0 from the following link (https://www.ni.com/en-gb/support/downloads/drivers/download.ni-visa.html#346210).
3. Download the NanoPro 1.0 software file from (https://github.com/jdanial/NanoPro) and unzip its contents to a new folder on the desktop renamed to ‘NanoPro 1.0’. Ensure the contents of the unzipped folder are as follows: two folders named [data] and [Dependencies], five files named [Configuration.csv], [Sequence.csv], [NanoPro 1.0_v1.3.aliases], [NanoPro 1.0_v1.3.exe] and [NanoPro 1.0_v1.3.ini].
4. Download and install the Kinesis 64-bit software for 64-bit windows from the following link (https://www.thorlabs.com/Software/Motion%20Control/KINESIS/Application/v1.14.28/KINESIS%20Install%20x64/kinesis_18247_setup_x64.exe). (https://www.thorlabs.com/Software/Motion%20Control/KINESIS/Application/v1.14.28/KINESIS%20Install%20x64/kinesis_18247_setup_x64.exe) Copy the contents from the folder path [C:\Program Files\Thorlabs\Kinesis] and paste them into the desktop folder path […\Nano Pro\Dependencies\Thorlabs].
5. Install the [PVCamSDK_Setup.exe] and [PMQI-LabViewSamples_Setup_1.2.2.1.exe] software files provided with the sCMOS camera (item 14 in Part 1). Copy the files [pvcam_helpher_-coloured_v1.dll] and [PVCamNET.dll] from the folder path [C:\Program Files\Photometrics\PMQI-LabViewSamples\Examples\2018\Dependencies] and paste them into the desktop folder path […\Nano Pro\Dependencies\Photometrics].
6. Request the drivers’ file from SmarAct (item 15 in Part 1). Unzip the contents of the drivers’ file and install the file [CDM21226_Setup.exe]. Install the [MCS2_Installer_2.1.3.exe] software file provided with the MSC2 control system (item 17 in Part 1). During installation, ensure that the check boxes for ‘MSC2 Tools and Programs’ and ‘Support for MSC2 with USB Interface’ are checked.
7. Download and install the 64-bit version of the Phidget control software from the following link (https://www.phidgets.com/downloads/phidget22/libraries/windows/Phidget22-x64.exe). Copy the contents from the folder path [C:\Program Files\Phidgets\Phidget22] and paste them into the desktop folder path […\Nano Pro\Dependencies\Phidgets].
8. Download and install ImageJ (item 139 in Part 1) from the following link (https://wsr.imagej.net/distros/win/ij153-win-java8.zip). Download and install ThunderSTORM from the following link (https://zitmen.github.io/thunderstorm/). Follow the installation instructions provided.
9. Open the [Configuration.csv] file in the folder unzipped in step 4. Edit the file using the following information:
a. Enter the serial number of the analog digital convertor device (item 44 in Part 1) in the field opposite to ‘Phidget 1 Serial Number’. The six digit serial number is printed on a white sticker fixed to the analog digital convertor device.

b. Enter the serial number of the control hub (item 45 in Part 1) in the field opposite to ‘Phidget 2 Serial Number’. The six digit serial number is printed on a white sticker fixed to the control hub.
c. Enter the serial number of the position aligner (item 18 in Part 1) in the field opposite to ‘Photo Sensitive Detector Serial Number’. The eight digit serial number is printed on a black sticker fixed to the position aligner.
d. Enter the COM port number of the four-position slider (item 67 in Part 1) in the field opposite to the ‘Filter Slider COM port’. To find the COM port number of the slider, type ‘device manager’ in the search box of Windows 10 located at the bottom left corner of the screen. Left-click the {Device Manager} tab that appears under the Best Match list. A long list of components will be shown. Browse to the component named ‘Ports (COM & LPT)’ and left-click the grey arrow on the left side of the component. The COM port number will be dropped-down.
10.Run the NanoPro 1.0 software by double-clicking the [NanoPro 1.0_v1.3.exe] software file in the ‘NanoPro 1.0’ folder. The NanoPro 1.0 software window should appear (see section 6: software window) as well as another blank camera view window. The [message box] (see section 6: software window) on the NanoPro 1.0 software window should display ‘Ready’. See Troubleshooting section in Part 1 if this message is not displayed.

Section 6: Software window

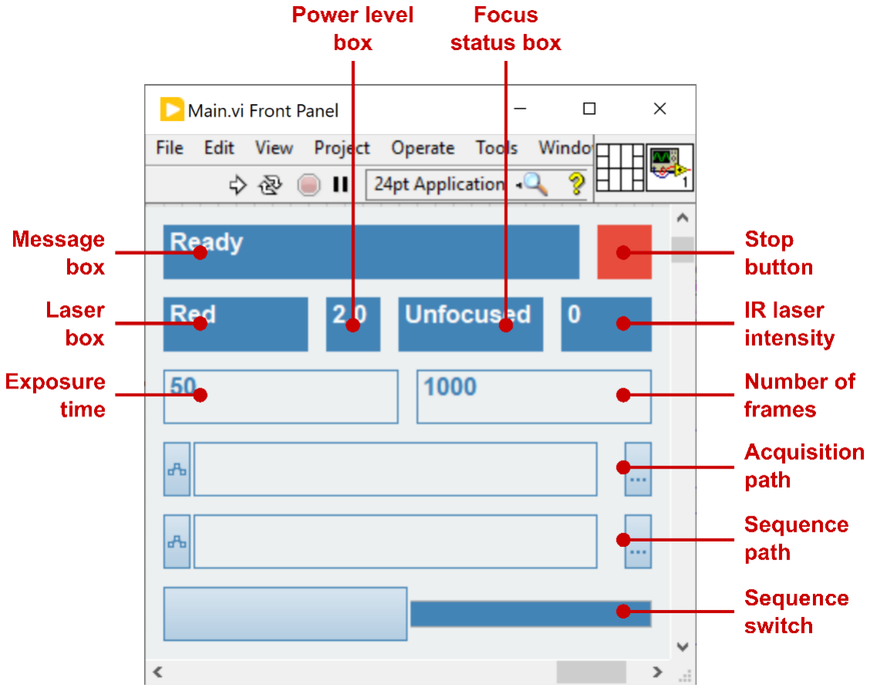
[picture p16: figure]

Figure 1 the NanoPro 1.0 software window. Components labelled in red are referred to between square brackets [] throughout the manual.

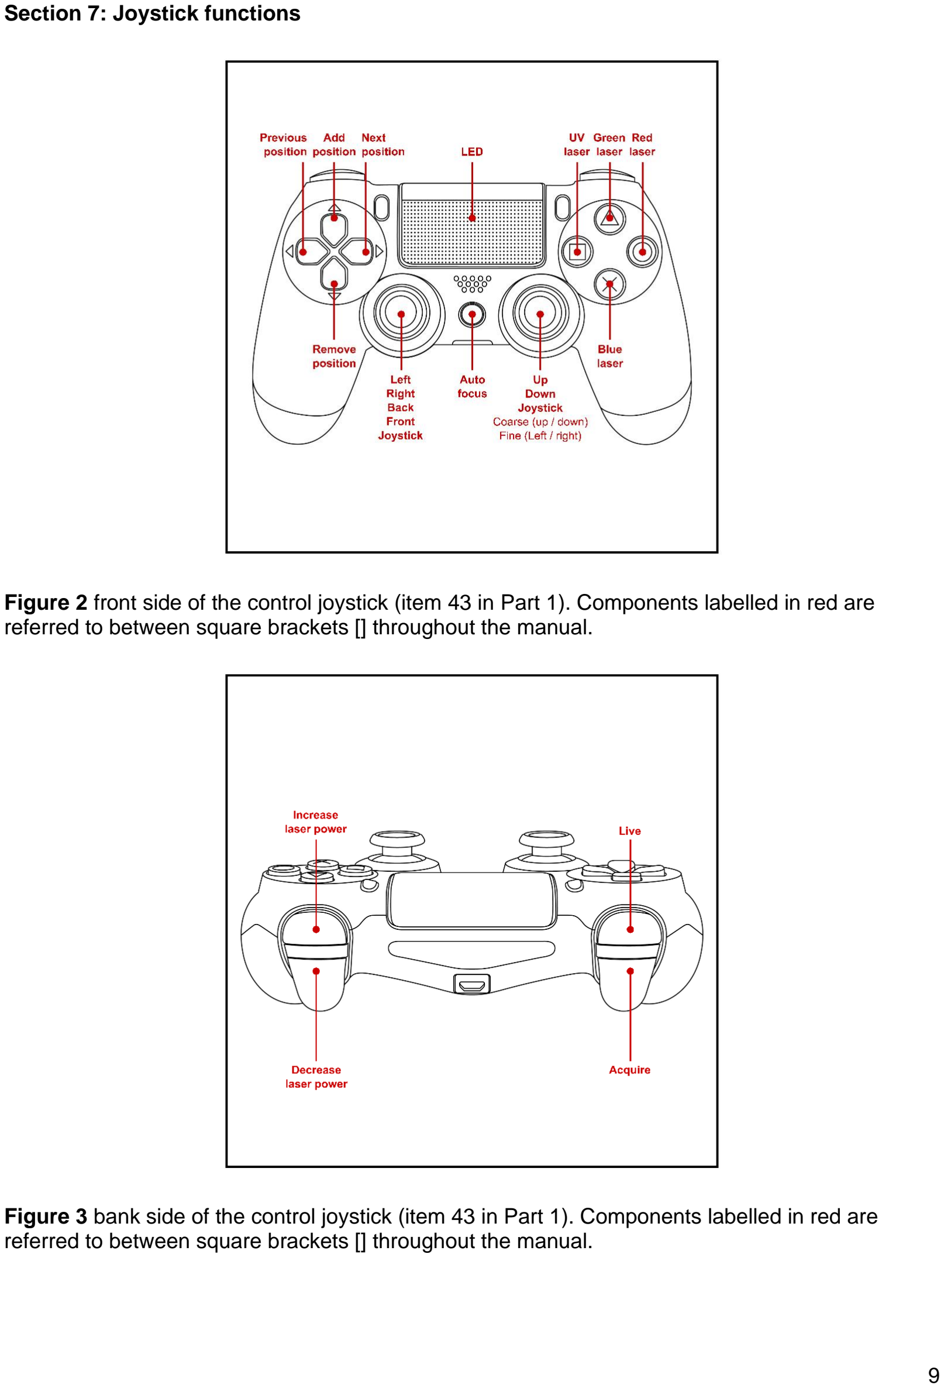
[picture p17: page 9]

Section 7: Joystick functions

Figure 2 front side of the control joystick (item 43 in Part 1). Components labelled in red are referred to between square brackets [] throughout the manual.

Figure 3 bank side of the control joystick (item 43 in Part 1). Components labelled in red are referred to between square brackets [] throughout the manual.

Section 8: Operation

Note:
Laser (excitation path) alignment, sample holder alignment, emission path alignment, focus stabilization system alignment, camera pixel size measurement, establishing microscope performance, and sample preparation & mounting are described in Part 1.

Subsection 8.1: Live imaging

1. Switch on the desired laser, ultra violet (405 nm), blue (488 nm), green (561 nm), or red (638 nm) lasers (items 3, 5, 6, or 7 respectively in Part 1), by pressing the [UV laser], [Blue laser], [Green laser], or [Red laser] buttons, respectively, on the control joystick (Figure 2). Alternatively, the LED can be switched on by pressing the [LED] button on the control joystick (Figure 2).
2. To activate live imaging, press the [Live] button on the control joystick (Figure 3). Laser / LED emission will start and ‘Live’ will be displayed in the [Message box] on the NanoPro 1.0 software window (Figure 1).
3. To de-activate live imaging, press the [Live] button on the control joystick. Laser / LED emission will stop and ‘Ready’ will be displayed in the [Message box] on the NanoPro 1.0 software window.

Subsection 8.2: Stage movement

4. The stage (i.e. positioners) can be moved left, right, back, or front by moving the [Left Right Back Front] joystick on the control joystick (Figure 2) left, right, back, or front, respectively.
5. The stage can be moved up or down by moving the [Up Down] joystick on the control joystick (Figure 2) up, or down, respectively, for coarse movement, or left, or right, respectively, for fine movement.

Subsection 8.3: Position recording

Note:
Only required for non-periodic multi-sample acquisitions.
6. Stage position can be recorded for multi-sample acquisitions by pressing the [Add position] button on the control joystick (Figure 2).
7. The last recording position can be removed by pressing the [Remove position] button on the control joystick (Figure 2).
8. The stage can be moved to recorded positions by pressing the [Next position] or [Previous position] buttons on the control joystick (Figure 2).

Subsection 8.4: Auto focusing

9. The imaging plane can be locked in focus if ‘Focused’ is displayed in the [Focus status box] on the NanoPro 1.0 software window (Figure 1). Press the [Auto focus] button on the control joystick (Figure 2) to lock the focus. ‘Locked’ should be displayed in the [Focus status box] on the NanoPro 1.0 software window.
10.Focus can be unlocked by pressing the [Auto focus] button on the control joystick (Figure 2). ‘Focused’ should be displayed in the [Focus status box] on the NanoPro 1.0 software window.

Subsection 8.5: Light source modulation

Note:
Step 10 applies to all lasers. Step 11 applies to LED.

11.Laser power can be increased or decreased by pressing the [Increase laser power] or [Decrease laser power] buttons, respectively. The voltage supplied to the intended laser should be displayed in the [Power level box].

Warning:
Do not increase the voltage supplied to the (638 nm) red laser (item 7 in Part 1) above 4V.

Subsection 8.6: Single acquisition

11.De-activate live imaging (step 3).
12.Set the [Exposure time] on the NanoPro 1.0 software window (Figure 1) to the desired exposure time (in milliseconds). Set the [Number of frames] on the NanoPro 1.0 software window to the desired number of frames to acquire.
13.Ensure a folder exists where the data is to be saved.
14.Select the acquisition path by pressing the button with the three dots on the [Acquisition path] on the NanoPro 1.0 software window. A dialogue prompt will appear from which the folder where the date is to be saved can be selected.
15.Press the [Acquire] button on the control joystick (figure 3) to start acquisition. Ensure ‘Acquire’ is displayed in the [Message box] on the NanoPro 1.0 software window. Gently rest the control joystick on the breadboard (item 64 in Part 1) to reduce perturbations to the microscope.
16.Wait until acquisition is complete or press the [Acquire] button on the control joystick to stop acquisition. Acquisition is complete or stopped when laser / LED emission is automatically de-activated and ‘Ready’ is displayed in the [Message box] on the NanoPro 1.0 software window.

Subsection 8.7: Multi sample acquisition

Note:
Ensure a spreadsheet software, such as Microsoft Excel, is installed on the computer before proceeding with next steps.

17.Open the [Sequence.csv] in the ‘NanoPro 1.0’ folder created in step 3 of section 5.
18.Edit the file using the following information:
a. Enter the number of times (i.e. repeats) the mounted sample is to be imaged in the field opposite to ‘Number of repeats’. As an example, if you are imaging each well in an ibidi ® µ-Slide 8 Well chambers twice, enter 2 in this field.
b. Enter the number of wells to be imaged in the direction parallel to the longer side of the optical table (item 63 in Part 1) in the field opposite to ‘Number of X wells’. As an example, if you are imaging all wells in an ibidi ® µ-Slide 8 Well chambers, enter 4 in this field. Beware that if you would like to image at non-periodic locations, the entry in this field will be ignored. Use the control joystick to record positions to acquire at (steps 6 to 8).
c. Enter the number of wells to be imaged in the direction parallel to the shorter side of the optical table in the field opposite to ‘Number of Y wells’. As an example, if you are imaging all wells in an ibidi ® µ-Slide 8 Well chambers, enter 2 in this field. Beware that if you would like to image at non-periodic locations, the entry in this field will be ignored.
d. Enter the number of Field Of Views (FOVs) to be imaged in the direction parallel to the longer side of the optical table in the field opposite to ‘Number of X FOVs’. As an example, if you are imaging 4 regions of each well, enter 4 in this field. Beware that the product of this field and the field opposite to ‘Number of Y FOVs’ has to equal the number of regions to be imaged in each well.
e. Enter the number of Field Of Views (FOVs) to be imaged in the direction parallel to the shorter side of the optical table in the field opposite to ‘Number of Y FOVs’. As an example, if you are imaging four regions of each well, enter 4 in this field. Beware that the product of this field and the field opposite to ‘Number of X FOVs’ has to equal the number of regions to be imaged in each well.
f. Enter the laser(s) to be used for imaging each region in the fields opposite to ‘Lasers’. Lasers will be switched on according to the sequence in which they are entered. As an example, if you would like to image each region using the (638 nm) red, then (561 nm) green, lasers (items 3 and 7 in Part 1), enter ‘Red’ in the field opposite to ‘Lasers’ and ‘Green’ in the field opposite to ‘Red’. Beware the first letter of each enter laser line has to be upper case.
g. Enter the distance between each well in the direction parallel to the longer side of the optical table in the field opposite to ‘X wells distance (um)’ in micrometres. As an example, if the distance between each well in the direction parallel to the longer side of the optical table is 4.5 mm, enter 4500 in this field. Beware that if you would like to image at non-periodic locations, the entry in this field will be ignored.
h. Enter the distance between each well in the direction parallel to the shorter side of the optical table in the field opposite to ‘Y wells distance (um)’ in micrometres. As an example, if the distance between each well in the direction parallel to the shorter side of the optical table is 4.5 mm, enter 4500 in this field. Beware that if you would like to image at non-periodic locations, the entry in this field will be ignored.
i. Enter the distance between each field of view in the direction parallel to the longer side of the optical table in the field opposite to ‘X FOVs distance (um)’ in micrometres. As an example, if the distance between each well in the direction parallel to the longer side of the optical table is 0.1 mm, enter 100 in this field.
j. Enter the distance between each field of view in the direction parallel to the shorter side of the optical table in the field opposite to ‘Y FOVs distance (um)’ in micrometres. As an example, if the distance between each well in the direction parallel to the shorter side of the optical table is 0.1 mm, enter 100 in this field.
k. Enter the number of frames to be imaged for each entered laser in the fields opposite to ‘Frames’. Each laser will be switched on for the number of frames entered. As an example, if you would like to acquire 10 frames with the red laser, then 10000 frames with green laser, enter 10 in the field opposite to ‘Frames’ and 10000 in the field opposite to 10.
l. [Optional, only for STORM imaging]. Enter the increase in the power of the (405 nm) ultra violet laser (item 5 in Part 1) after a set duration (see step 18m) in the field opposite to ‘UV activation step intensity (V)’ in volts. As an example, if you would like to increase the power of the ultra violet laser in steps of 0.1 V, enter 0.1 in the field opposite to ‘UV activation step intensity (V)’. Beware, if you are not performing STORM imaging, or would not like to use an activation laser, enter 0 in the field opposite to ‘UV activation step intensity (V)’.

m. [Optional, only for STORM imaging]. Enter the time duration after which the power of the ultra violet laser is increased (see step 18m) in the field opposite to ‘UV activation step duration (min)’ in minutes. As an example, if you would like to increase the power of the ultra violet laser after every 10 minutes, enter 10 in the field opposite to ‘UV activation step duration (min)’. Beware, if you are not performing STORM imaging, or would not like to use an activation laser, enter 1000 in the field opposite to ‘UV activation step duration (min)’.
19.If periodic imaging is to be performed (i.e. no positions were recorded using the control joystick), move the positioners to the centre of the well on the back / right corner of the sample using the control joystick (step 4).
20.Switch on each laser entered in step 18f using the control joystick, one after the other (step 1). Increase, or decrease, the power of each laser (step 11).
21.Activate live imaging (step 2).
22.Move the positioners (item 15) downwards (coarse or fine) using the control joystick (step 5) to focus the sample as described in Part 1.
23.Activate the autofocus system (step 9).
24.Deactivate live imaging (step 3).
25.Select the [Sequence path] by pressing the button with the three dots on the [Sequence path] on the NanoPro 1.0 software window. A dialogue prompt will appear from which the [Sequence.csv] file can be chosen.
26.Toggle the [Sequence switch] on the NanoPro 1.0 software window (Figure 1).
27.Perform steps 12 to 16.

Subsection 8.8: Switching off software

28.Press the [Stop] button on the NanoPro 1.0 software window (Figure 1). Close the NanoPro 1.0 software window.

Note:
Refer to Part 1 to switch off the entire microscope.

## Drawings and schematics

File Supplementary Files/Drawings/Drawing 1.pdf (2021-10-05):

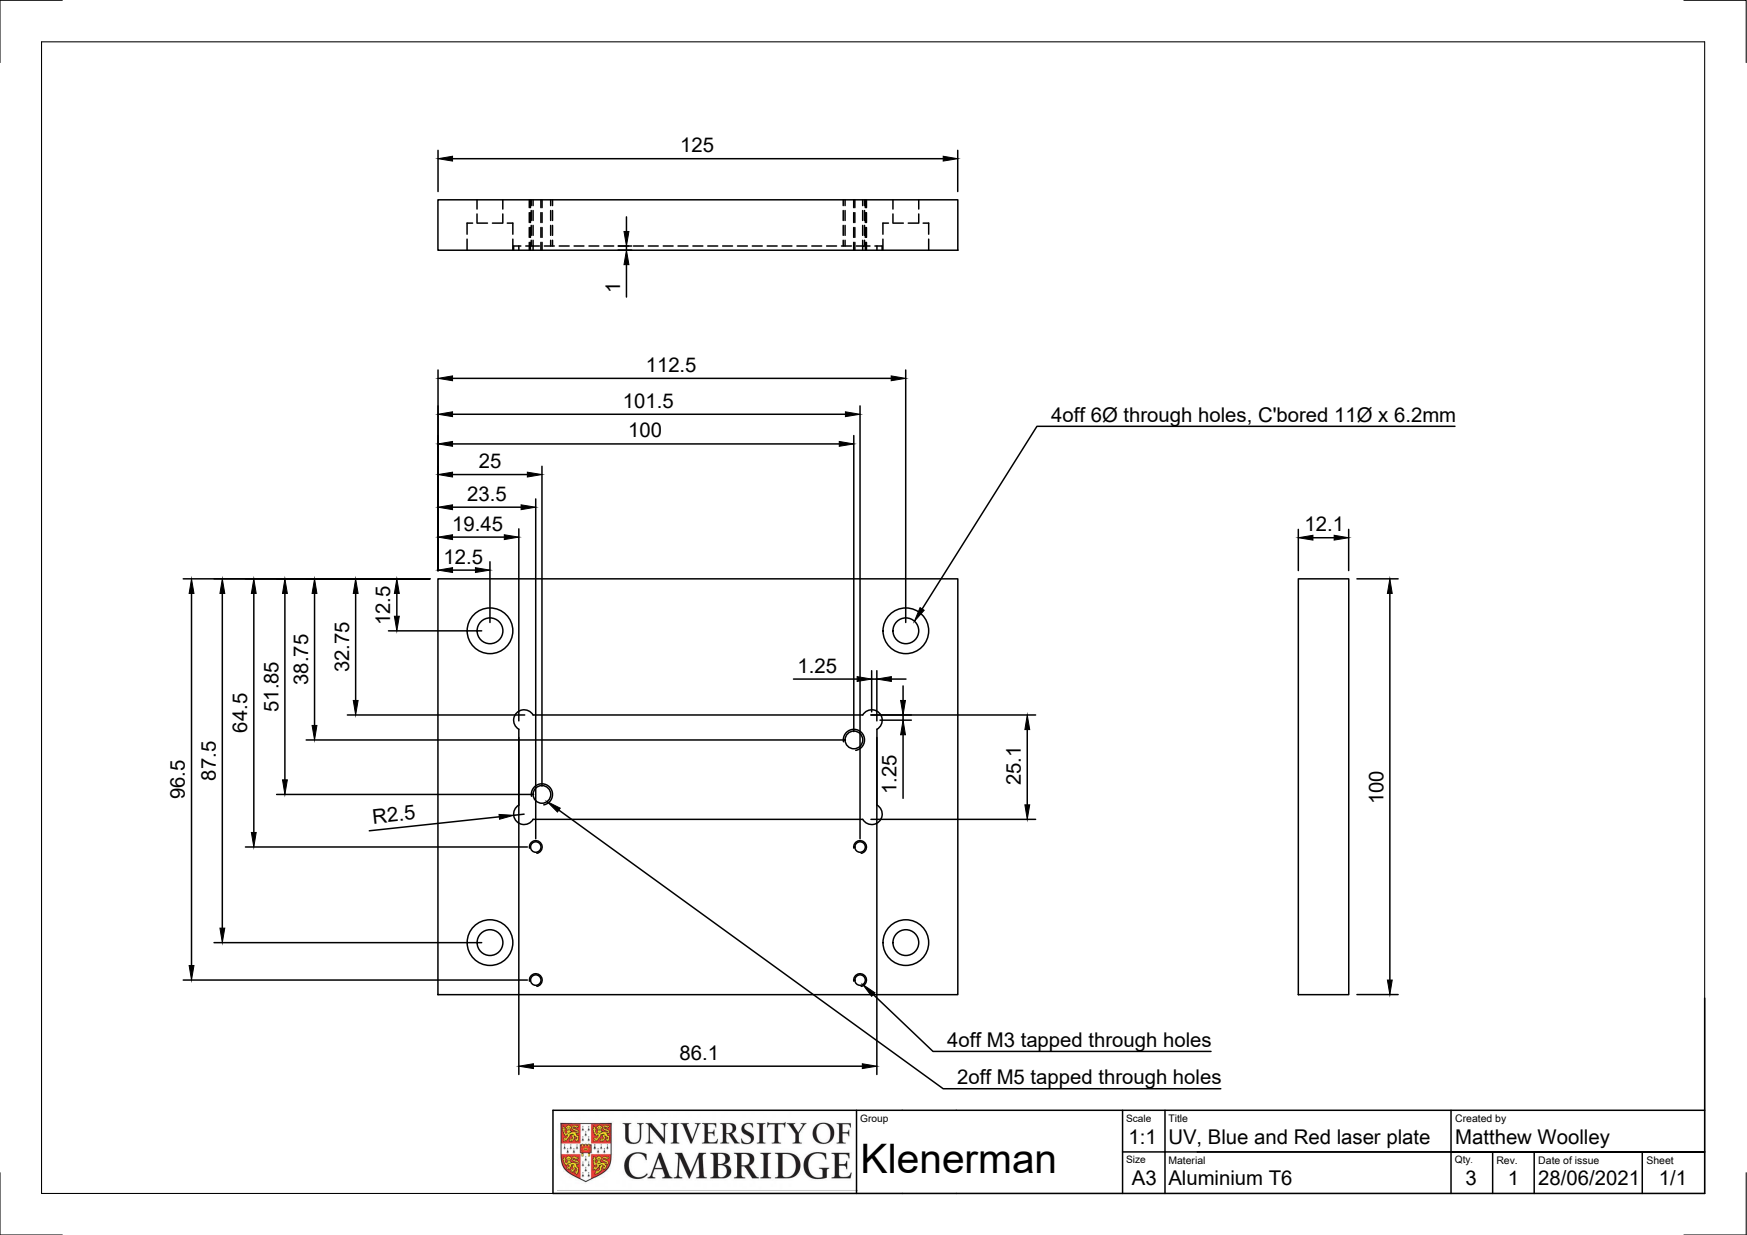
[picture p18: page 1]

4off 6Ø through holes, C'bored 11Ø x 6.2mm

4off M3 tapped through holes

2off M5 tapped through holes

Group | Scale 1:1 Klenerman A3 | Title UV, Blue and Red laser plate | Created by Matthew Woolley

Size | Material Aluminium T6 | Qty. 3 | Rev. 1 | Date of issue 28/06/2021 | Sheet 1/1

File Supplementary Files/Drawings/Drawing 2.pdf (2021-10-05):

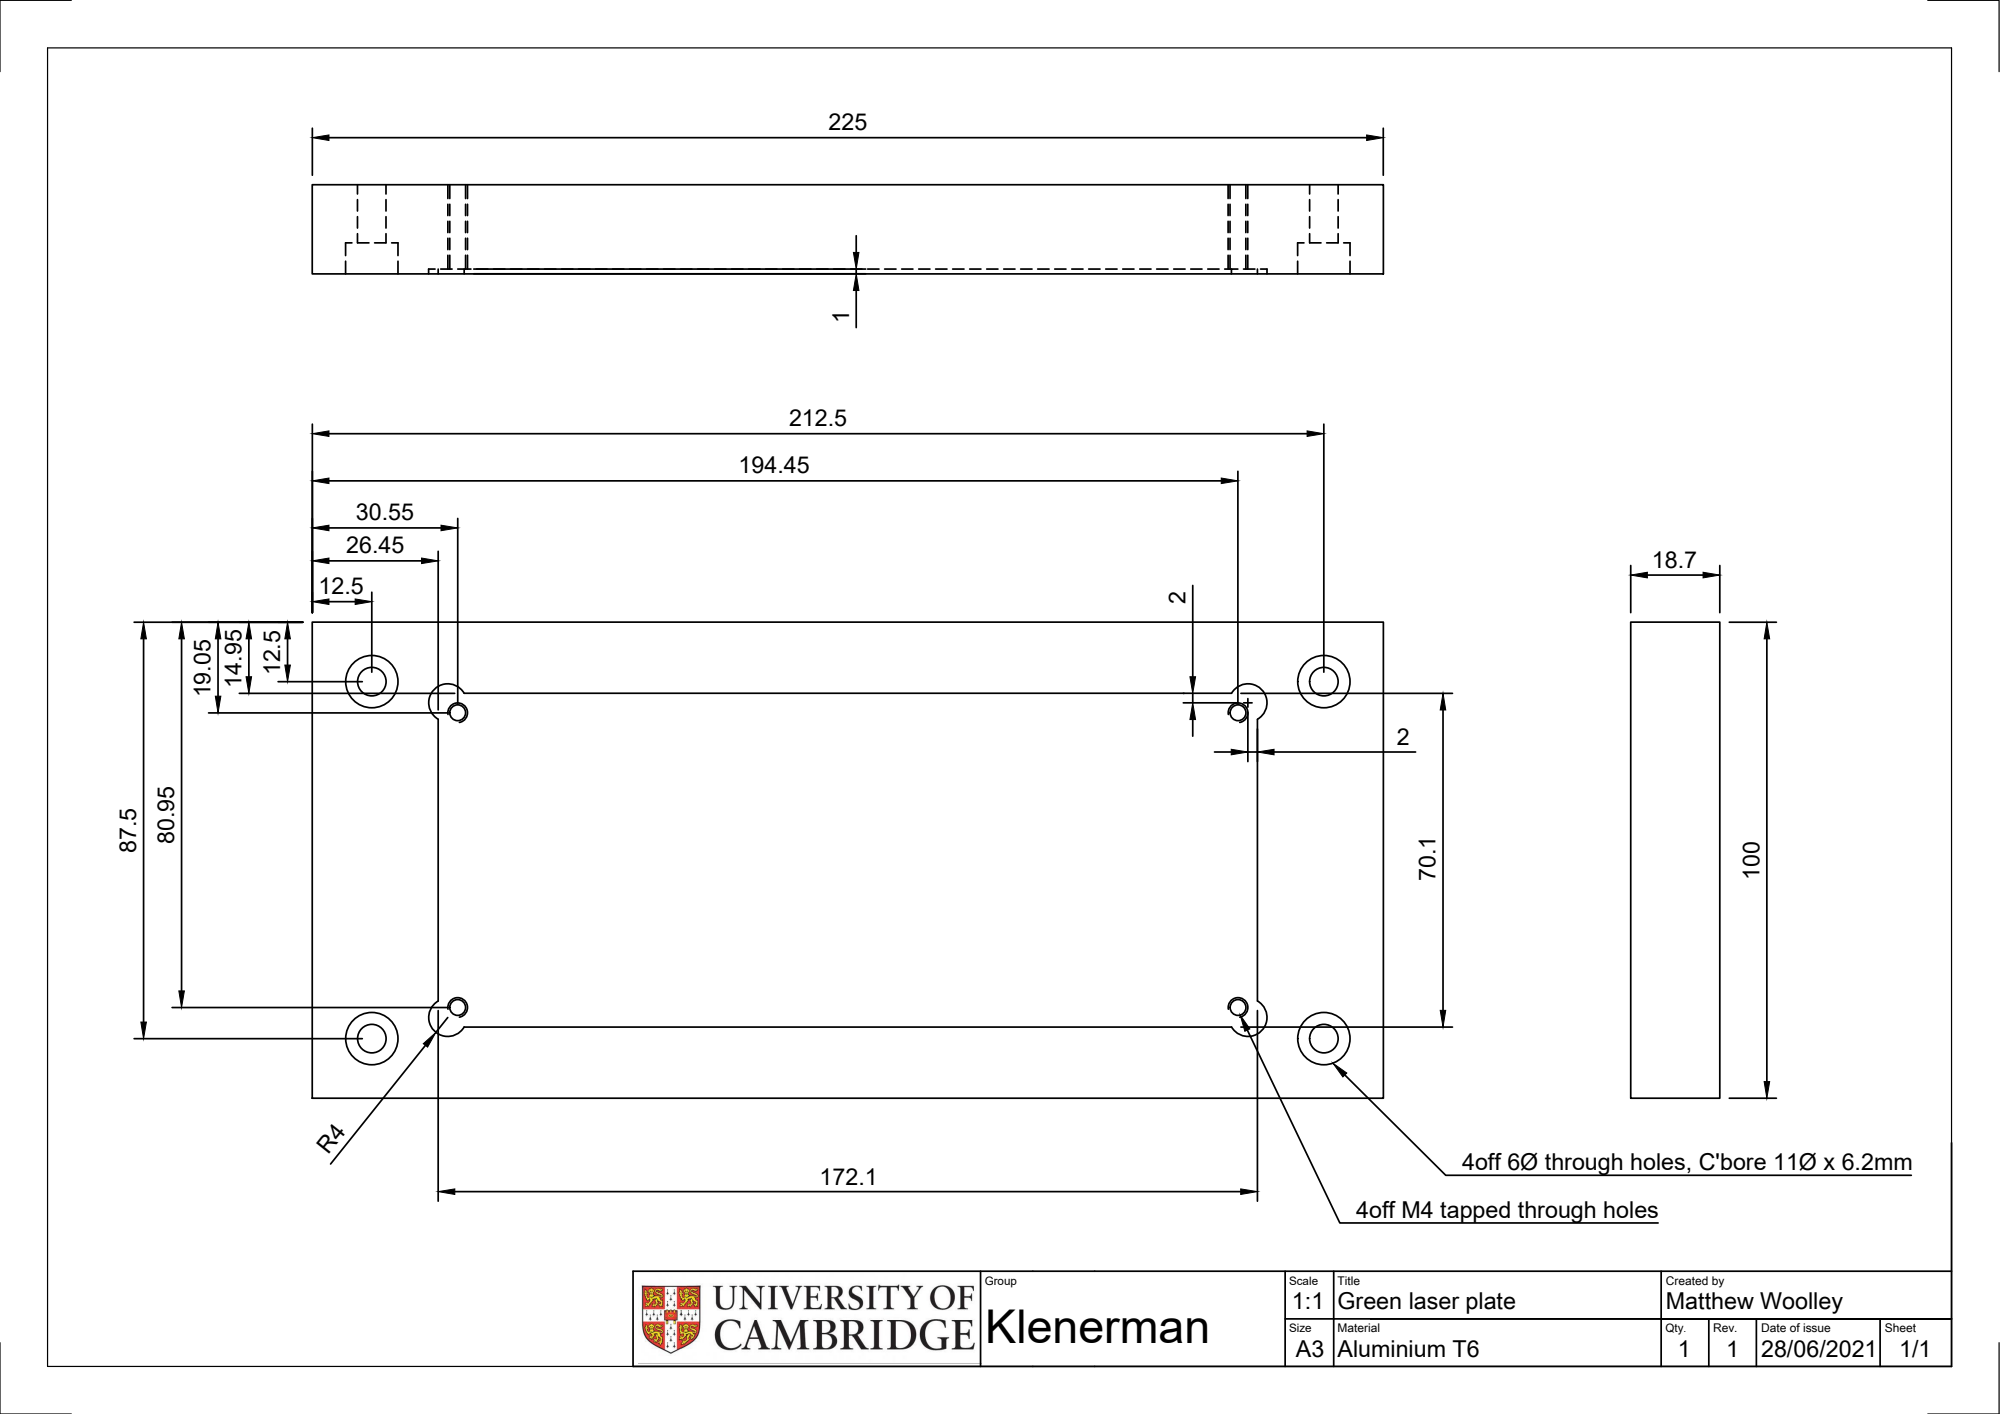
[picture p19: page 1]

4off 6Ø through holes, C'bore 11Ø x 6.2mm

4off M4 tapped through holes

Group | Scale 1:1 Klenerman A3 | Title Green laser plate | Created by Matthew Woolley

Size | Material Aluminium T6 | Qty. 1 | Rev. 1 | Date of issue 28/06/2021 | Sheet 1/1

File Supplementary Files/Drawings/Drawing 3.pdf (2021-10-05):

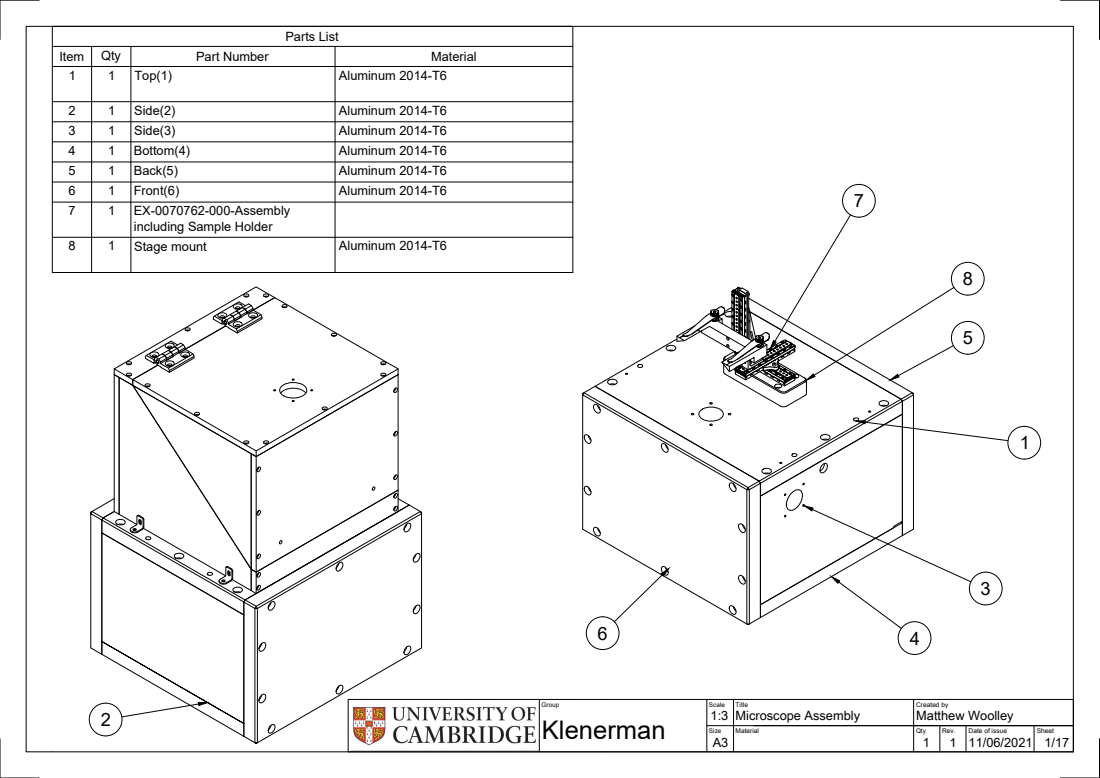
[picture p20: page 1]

Parts List

Item | Qty | Part Number | Material
1 | 1 | Top(1) | Aluminum 2014-T6

2 | 1 | Side(2) | Aluminum 2014-T6
3 | 1 | Side(3) | Aluminum 2014-T6
4 | 1 | Bottom(4) | Aluminum 2014-T6
5 | 1 | Back(5) | Aluminum 2014-T6
6 | 1 | Front(6) | Aluminum 2014-T6
7 | 1 | EX-0070762-000-Assembly including Sample Holder

8 | 1 | Stage mount | Aluminum 2014-T6

Group | Scale 1:3 Klenerman A3 | Title Microscope Assembly | Created by Matthew Woolley

Size | Material | Qty. 1 | Rev. | Date of issue 11/06/2021 | Sheet 1/17

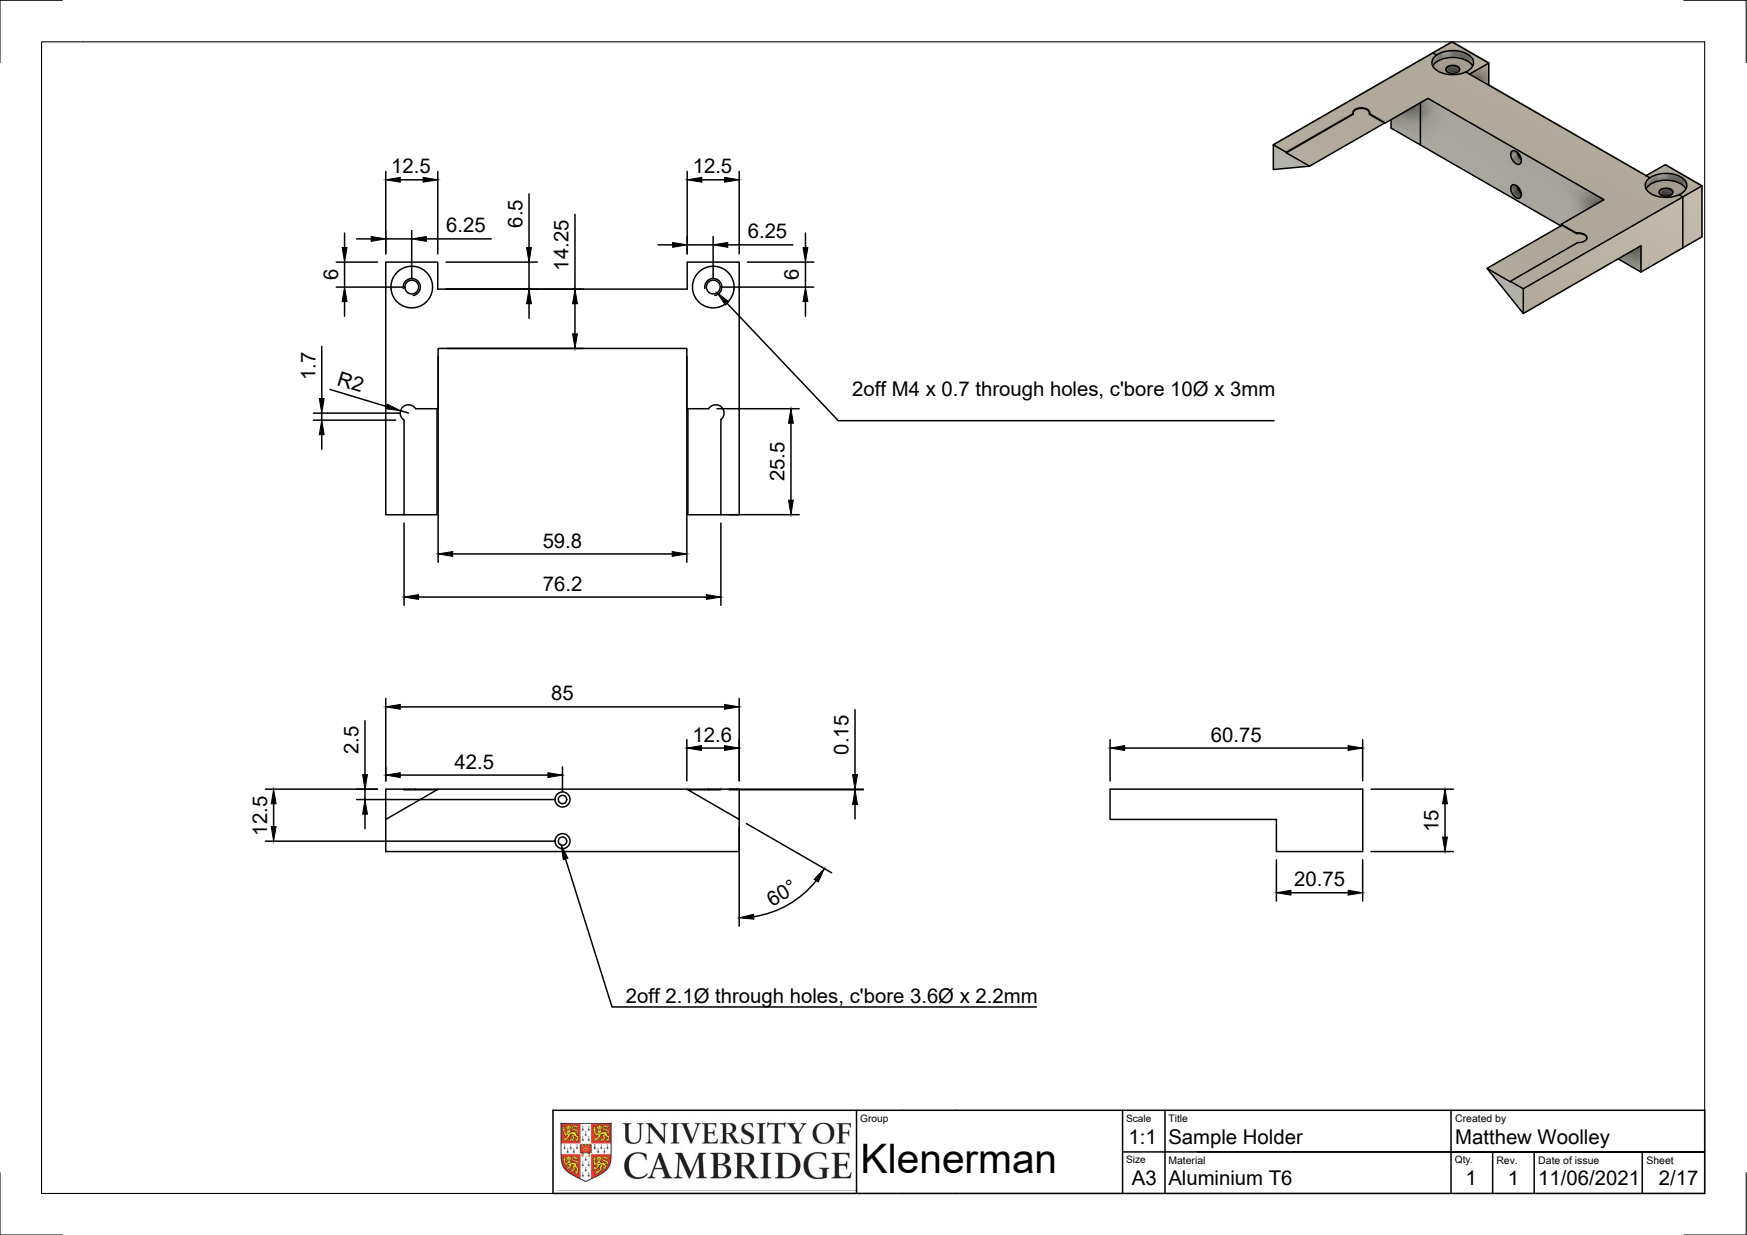
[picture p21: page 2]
2off 2.1Ø through holes, c'bore 3.6Ø x 2.2mm 1.7

2off M4 x 0.7 through holes, c'bore 10Ø x 3mm 0.15

Group | Scale 1:1 Klenerman A3 | Title Sample Holder | Created by Matthew Woolley

Aluminium T6 | 1 | | 11/06/2021 | 2/17

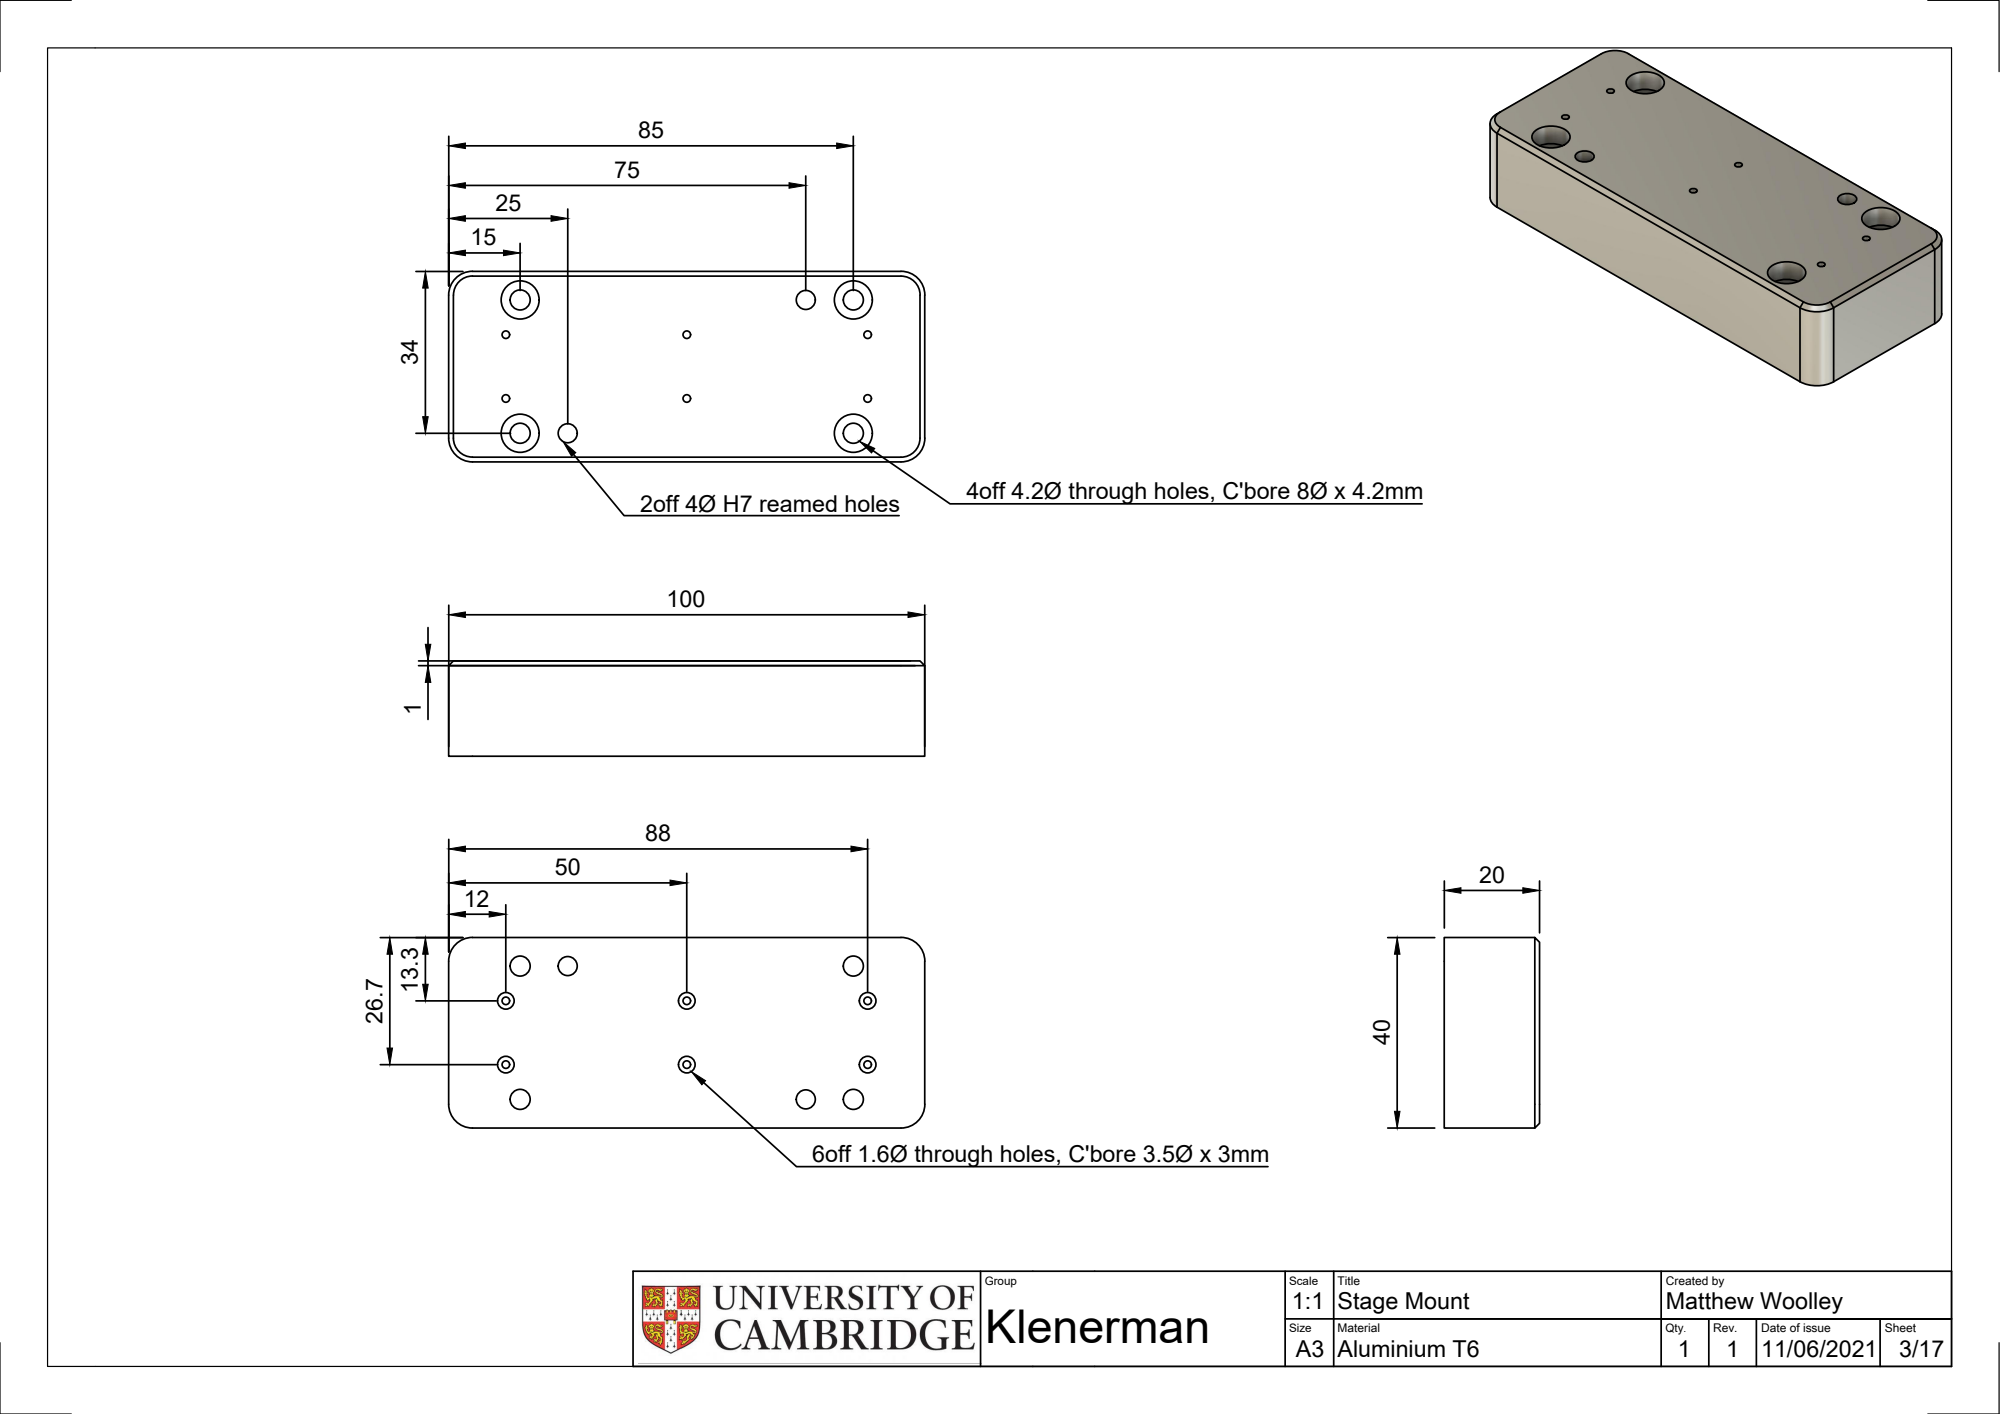
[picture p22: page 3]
2off 4Ø H7 reamed holes; 4off 4.2Ø through holes, C'bore 8Ø x 4.2mm

6off 1.6Ø through holes, C'bore 3.5Ø x 3mm

Group | Scale 1:1 Klenerman A3 | Title Stage Mount | Created by Matthew Woolley

Aluminium T6 | 1 | | 11/06/2021 | 3/17

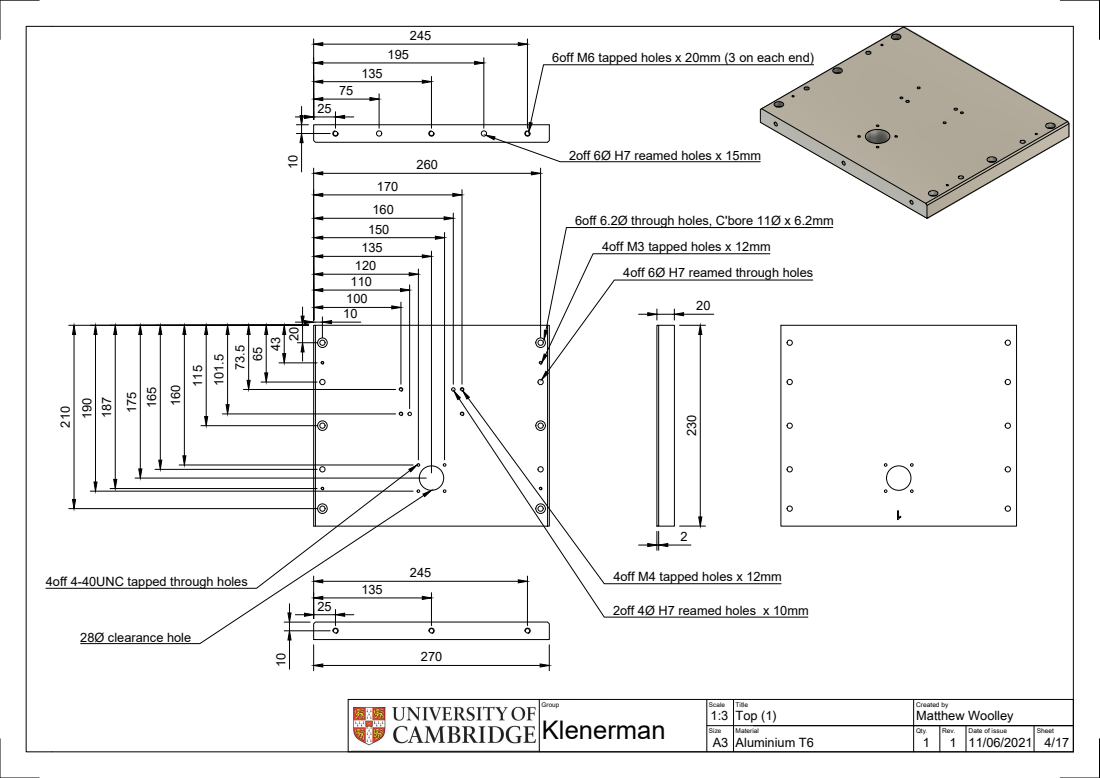
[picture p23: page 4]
2off 6Ø H7 reamed holes x 15mm; 4off M3 tapped holes x 12mm; 4off M4 tapped holes x 12mm; 2off 4Ø H7 reamed holes x 10mm; 28Ø clearance hole

6off M6 tapped holes x 20mm (3 on each end)

6off 6.2Ø through holes, C'bore 11Ø x 6.2mm

4off 6Ø H7 reamed through holes

4off 4-40UNC tapped through holes

Group | Scale 1:3 Klenerman A3 | Title Top (1) | Created by Matthew Woolley

Aluminium T6 | 1 | | 11/06/2021 | 4/17

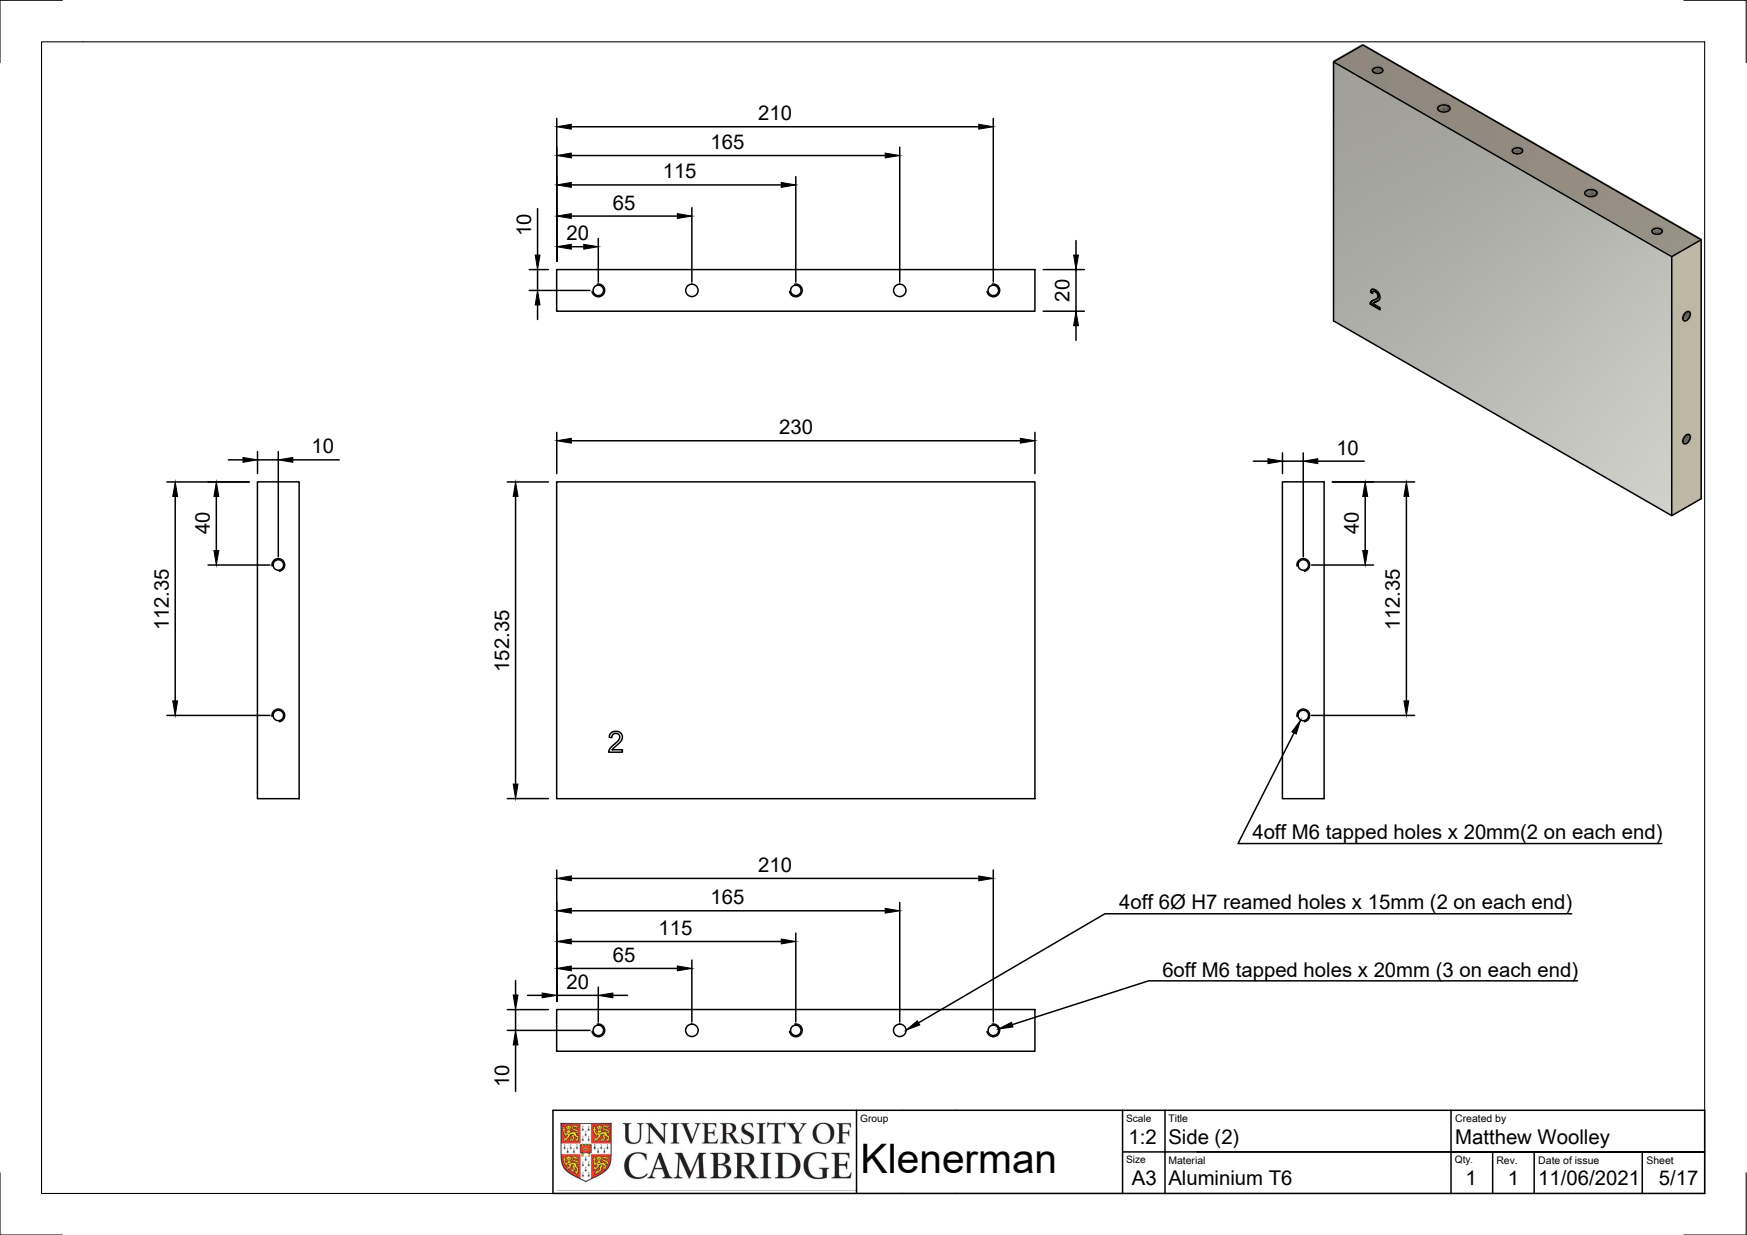
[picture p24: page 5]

4off M6 tapped holes x 20mm(2 on each end) 20

4off 6Ø H7 reamed holes x 15mm (2 on each end)

6off M6 tapped holes x 20mm (3 on each end)

Group | Scale 1:2 Klenerman A3 | Title Side (2) | Created by Matthew Woolley

Aluminium T6 | 1 | | 11/06/2021 | 5/17

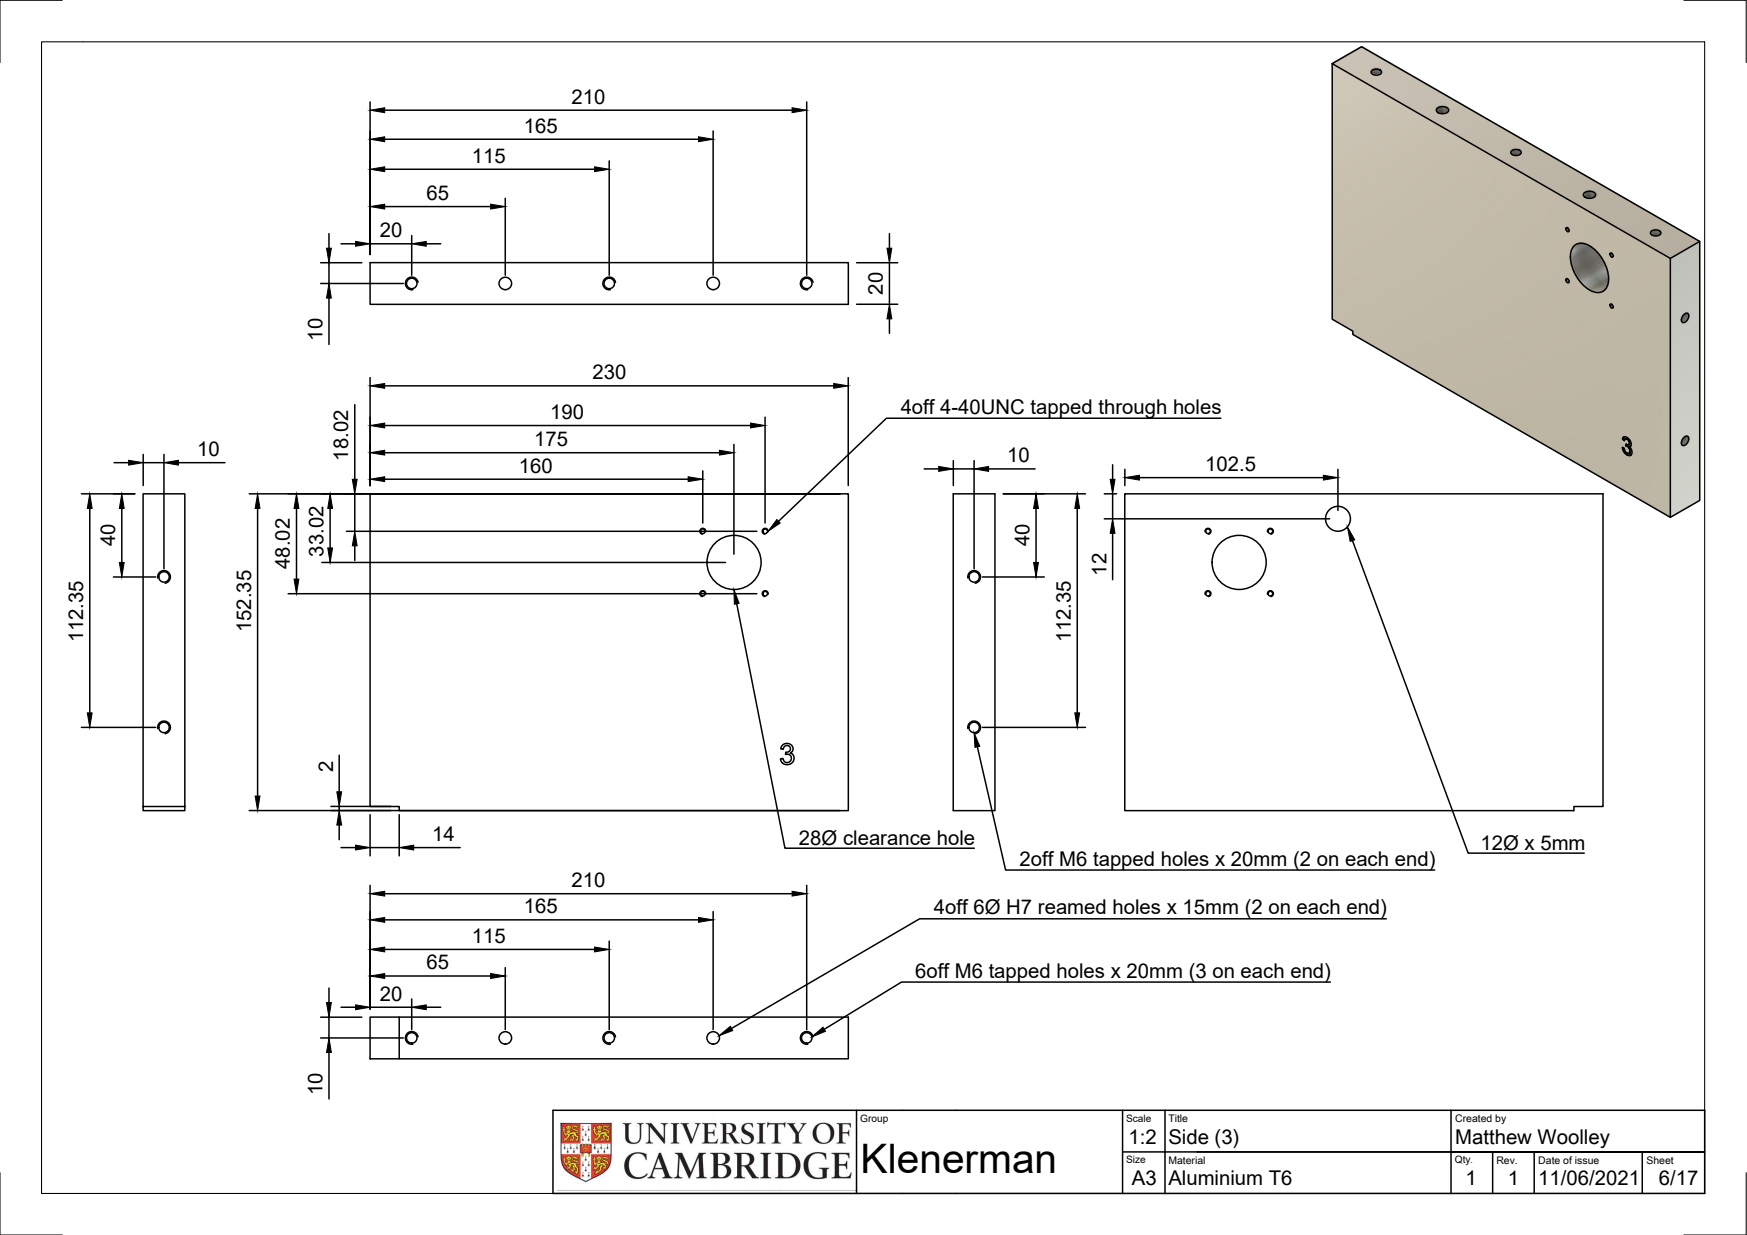
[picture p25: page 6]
28Ø clearance hole

4off 4-40UNC tapped through holes

2off M6 tapped holes x 20mm (2 on each end)

4off 6Ø H7 reamed holes x 15mm (2 on each end)

6off M6 tapped holes x 20mm (3 on each end)

Group | Scale | Title Side (3) | Created by Matthew Woolley

Aluminium T6 | 1 | | 11/06/2021 | 6/17

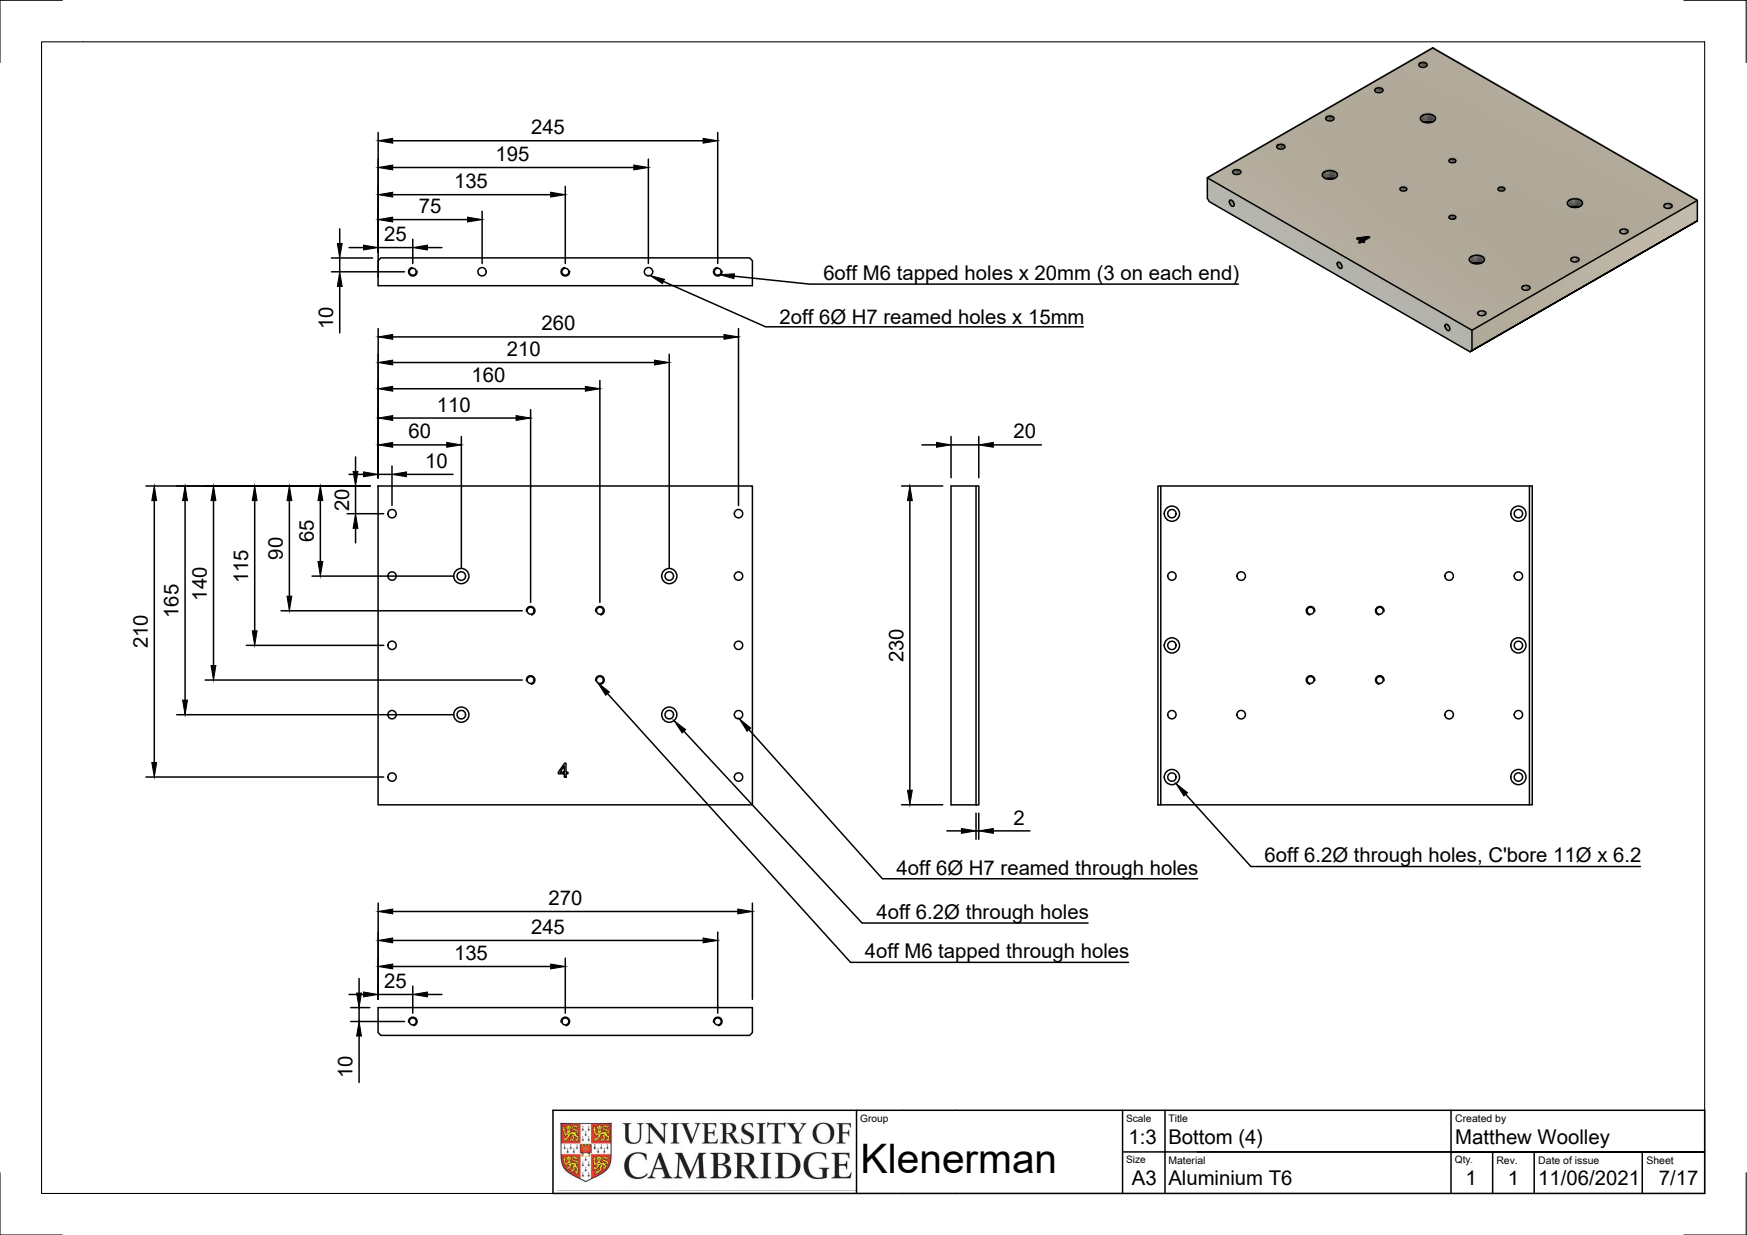
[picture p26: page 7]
2off 6Ø H7 reamed holes x 15mm; 4off 6.2Ø through holes

6off M6 tapped holes x 20mm (3 on each end)

6off 6.2Ø through holes, C'bore 11Ø x 6.2

4off 6Ø H7 reamed through holes

4off M6 tapped through holes

Group | Scale 1:3 Klenerman A3 | Title Bottom (4) | Created by Matthew Woolley

Aluminium T6 | 1 | | 11/06/2021 | 7/17

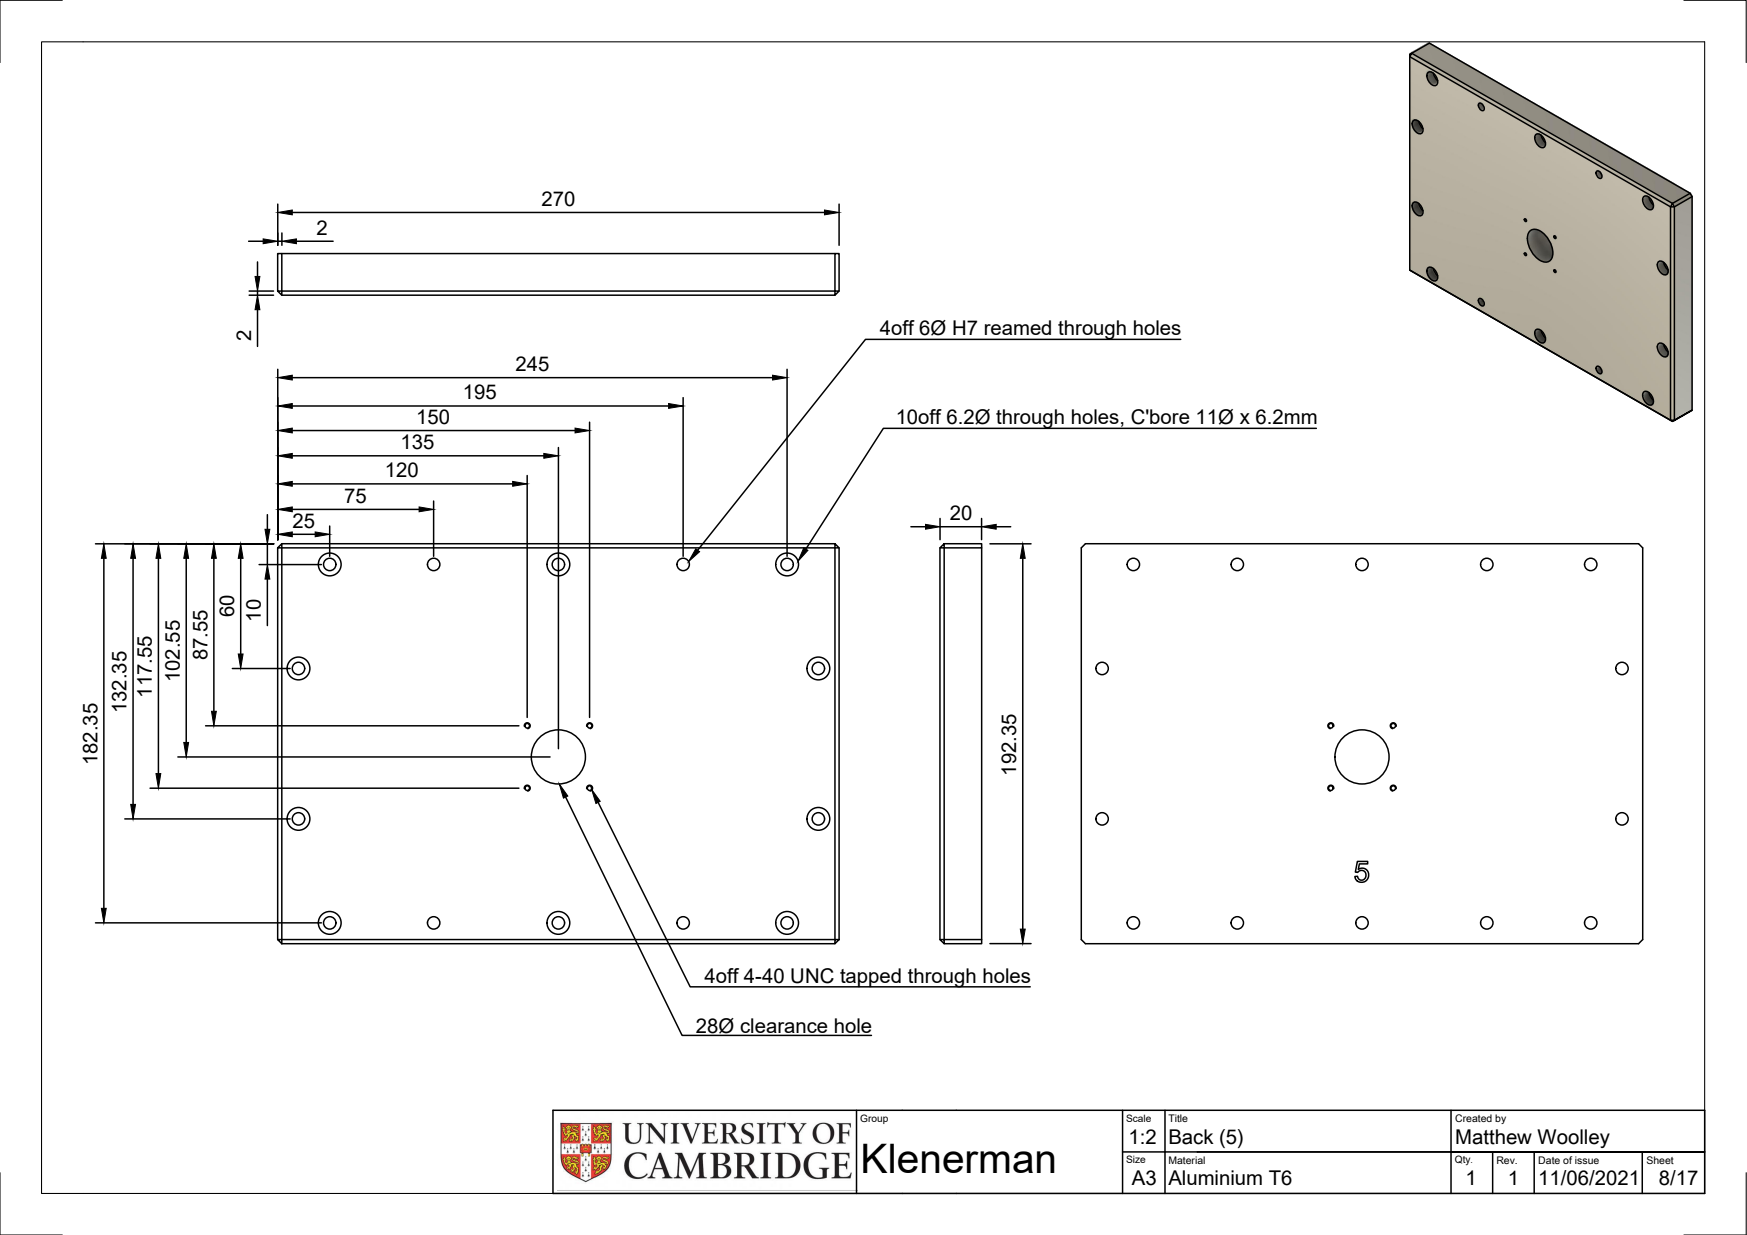
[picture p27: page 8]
28Ø clearance hole

4off 6Ø H7 reamed through holes

10off 6.2Ø through holes, C'bore 11Ø x 6.2mm

4off 4-40 UNC tapped through holes

Group | Scale | Title Back (5) | Created by Matthew Woolley

Aluminium T6 | 1 | | 11/06/2021 | 8/17

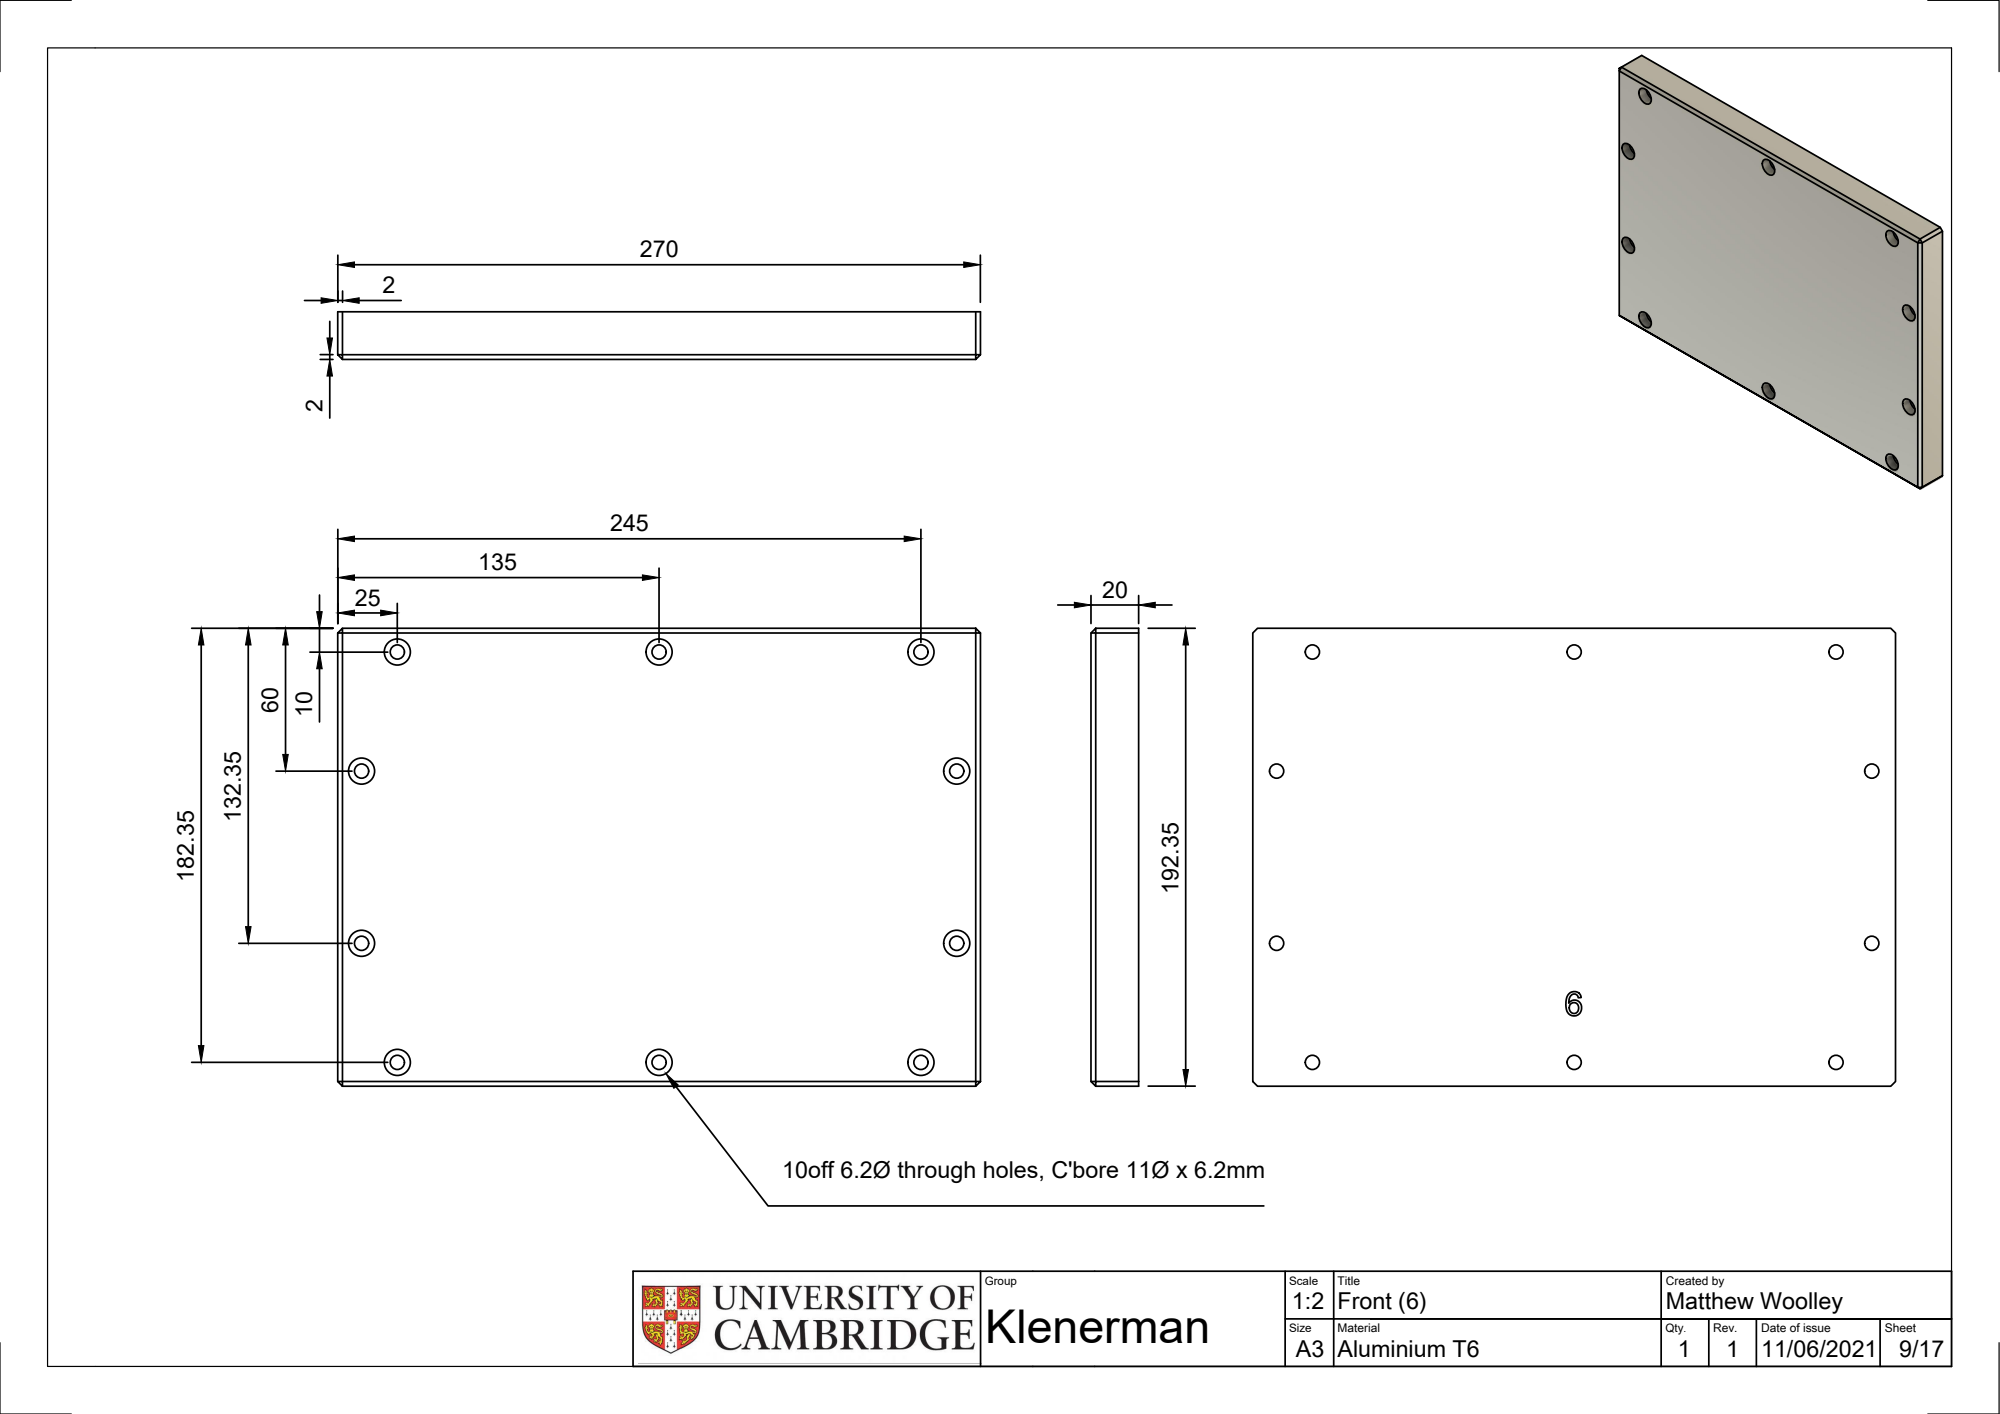
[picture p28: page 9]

10off 6.2Ø through holes, C'bore 11Ø x 6.2mm

Group | Scale | Title Front (6) | Created by Matthew Woolley

Aluminium T6 | 1 | | 11/06/2021 | 9/17

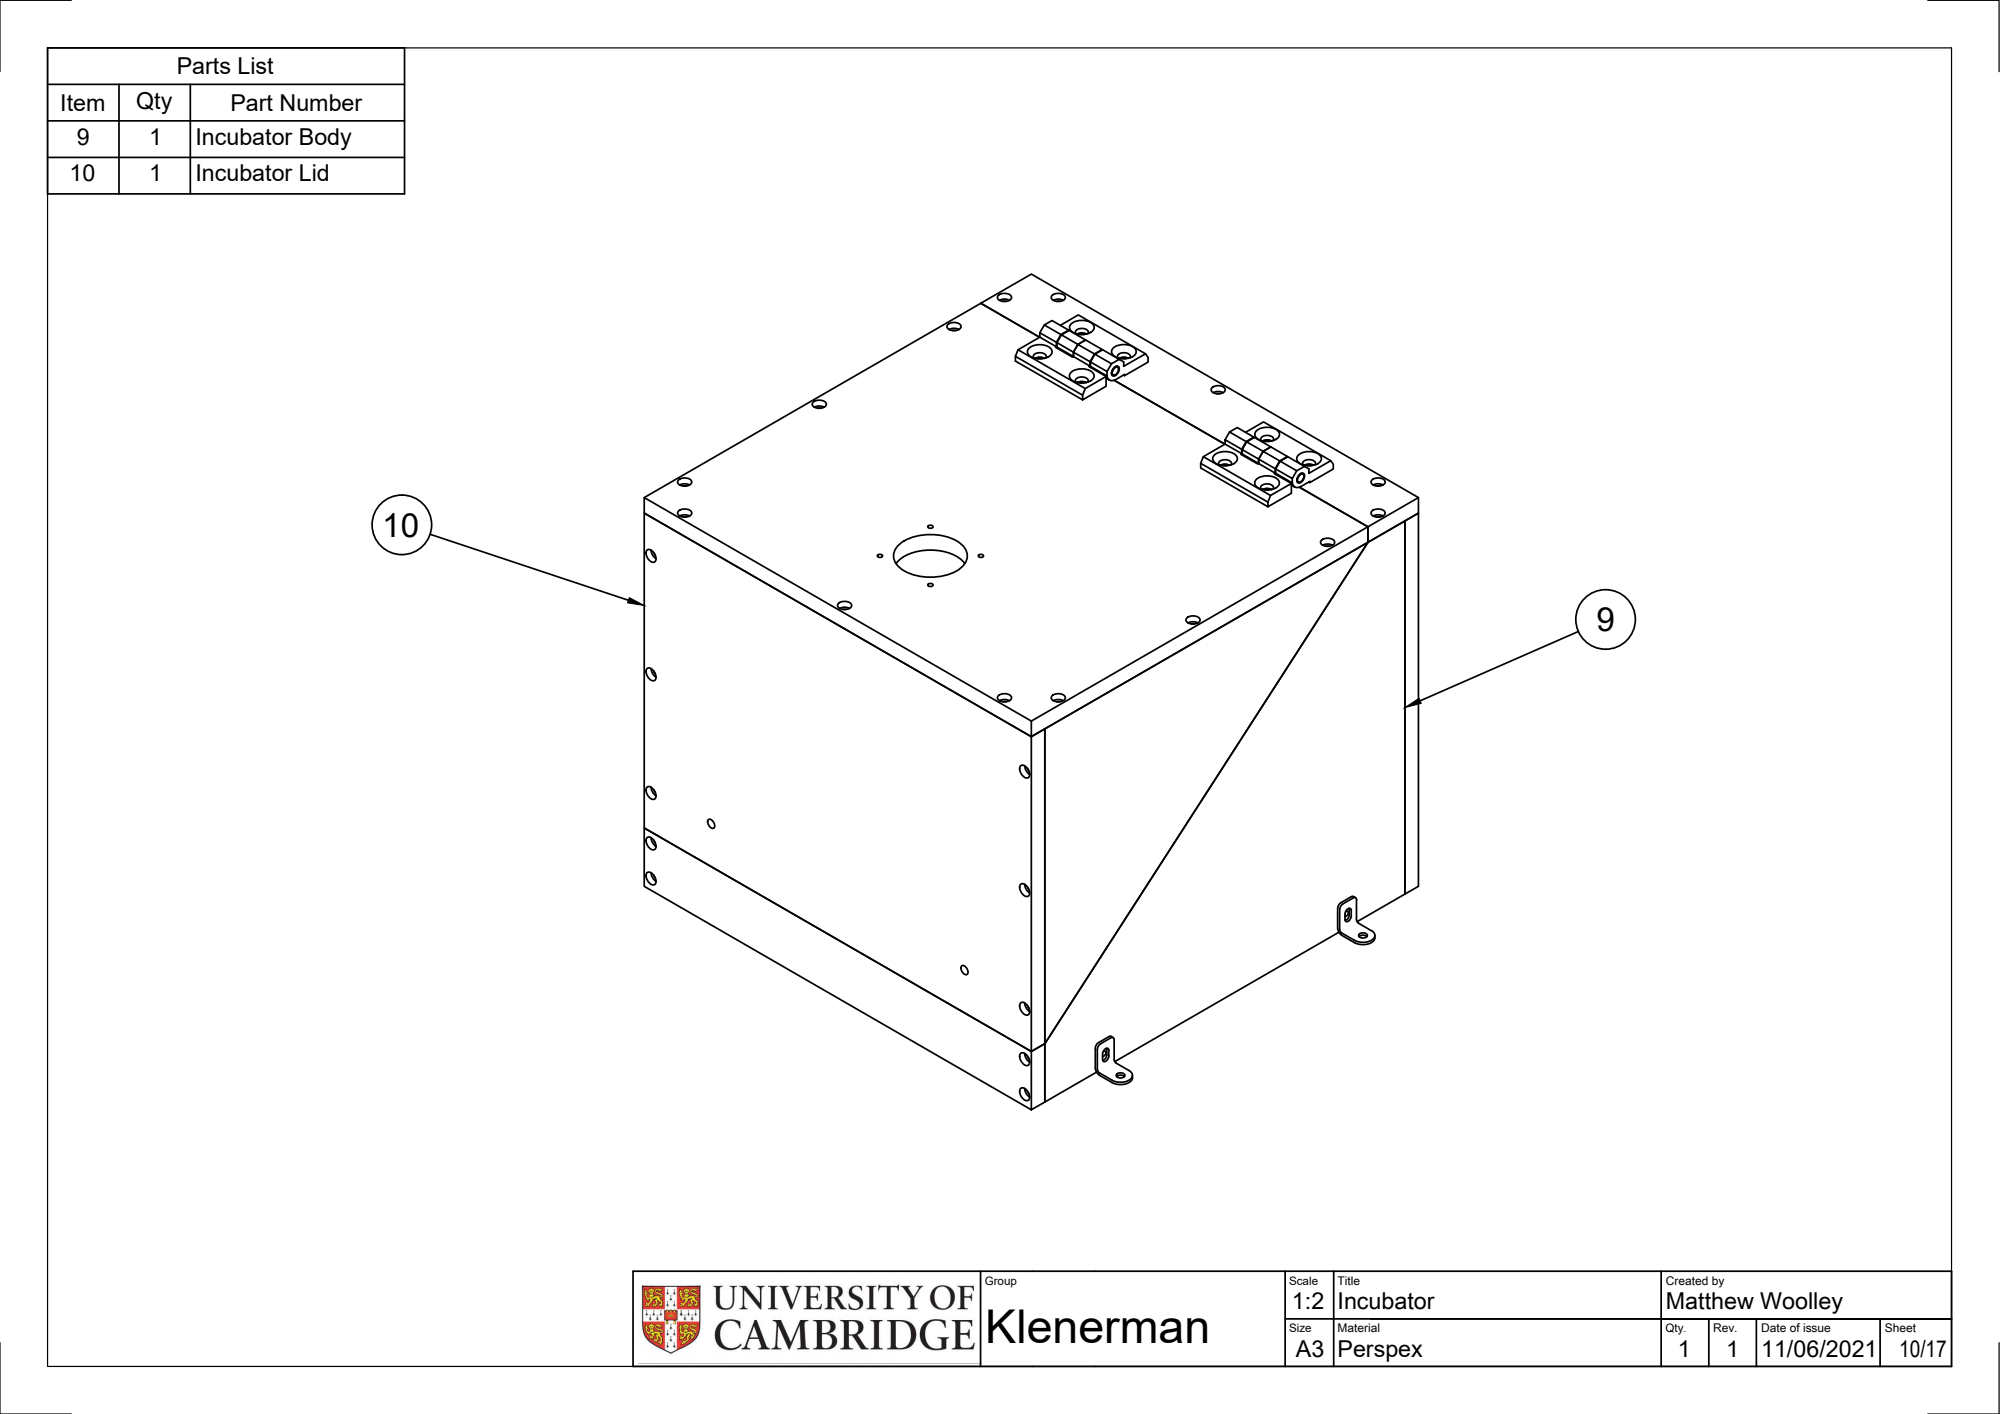
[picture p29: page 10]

Parts List

Item | | Qty | Part Number
9 | | 1 | Incubator Body
10 | | 1 | Incubator Lid

Group | Scale | Title Incubator | Created by Matthew Woolley

Perspex | 1 | | 11/06/2021 | 10/17


6off 3.2Ø through holes, C'bore 6Ø x 3.2mm

Group | Scale | Title Incubator Body-Back Panel | Created by Matthew Woolley

Perspex | 1 | | 11/06/2021 | 11/17

6off M3 tapped holes x 10mm

2off M3 tapped through holes

Group | Scale | Title Incubator Body-Side Panel | Created by Matthew Woolley

Perspex | 2 | | 11/06/2021 | 12/17


5off 3.2Ø through holes, C'bore 6Ø x 3.2mm

4off M5 tapped through holes

Group | Scale | Title Incubator Body-Top Panel | Created by Matthew Woolley

Perspex | 1 | | 11/06/2021 | 13/17


4off 3.2Ø through holes, C'bore 6Ø x 3.2mm

Group | Scale | Title Incubator Body-Front Panel | Created by Matthew Woolley

Perspex | 1 | | 11/06/2021 | 14/17

28Ø clearance hole

4off M5 tapped through holes

9off 3.2Ø through holes, C'bore 6Ø x 3.2mm

4off 4-40 UNC tapped through holes

Group | Scale | Title Incubator Lid-Top Panel | Created by Matthew Woolley

Perspex | 1 | | 11/06/2021 | 15/17

3off M3 tapped holes x 10mm

6off 3.2Ø through holes, C'bore 6Ø x 3.2mm

2off M5 tapped through holes

Group | Scale | Title Incubator Lid-Front Panel | Created by Matthew Woolley

Perspex | 1 | | 11/06/2021 | 16/17

6off M3 tapped holes x 10mm

Group | Scale | Title Incubator Lid-Side Panel | Created by Matthew Woolley
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

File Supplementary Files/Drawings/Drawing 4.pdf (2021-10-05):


Parts List

Item | Qty | Part Number
1 | 1 | Construction rails
2 | 1 | Lid

3 | 1 | Side Panel 1

4 | 1 | Side panel 2

5 | 1 | Side panel 3

6 | 1 | Side panel 4

Group | Scale 1:4 Klenerman A3 | Title Laser Enclosure | Created by Matthew Woolley

Size | Material | Qty. 1 | Rev. | Date of issue 29/06/2021 | Sheet 1/6


Re-drill and tap M6 x15mm after cutting rail down to 170mm

Group | Scale 1:2 Klenerman A3 | Title Laser Enclosure | Created by Matthew Woolley

Thor Labs-XE25L225/M Modified | 4 | | 29/06/2021 | 2/6


Group | Scale 1:4 Klenerman A3 | Title Lid | Created by Matthew Woolley

Palight PVC Foam Board | 1 | | 29/06/2021 | 3/6


Group | Scale 1:3 Klenerman A3 | Title Side Panel 1 | Created by Matthew Woolley

Palight PVC Foam Board | 1 | | 29/06/2021 | 4/6


Group | Scale | Title Side Panel 2 | Created by Matthew Woolley

Palight PVC Foam Board | 1 | | 29/06/2021 | 5/6


Group | Scale | Title Side Panels 3 and 4 | Created by Matthew Woolley

Palight PVC Foam Board | 2 | | 29/06/2021 | 6/6

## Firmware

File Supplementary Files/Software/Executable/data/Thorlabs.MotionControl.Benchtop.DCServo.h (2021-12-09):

// summary:	Declares the functions class
// The following ifdef block is the standard way of creating macros which make exporting 
// from a DLL simpler. All files within this DLL are compiled with the BENCHTOPDCSERVO_EXPORTS
// symbol defined on the command line. This symbol should not be defined on any project
// that uses this DLL. This way any other project whose source files include this file see 
// BENCHTOPDCSERVO_API functions as being imported from a DLL, whereas this DLL sees symbols
// defined with this macro as being exported.

#pragma once

#ifdef BENCHTOPDCSERVODLL_EXPORTS
/// <summary> Gets the Benchtop DCServo API. </summary>
#define BENCHTOPDCSERVO_API __declspec(dllexport)
#else
#define BENCHTOPDCSERVO_API __declspec(dllimport)
#endif

#include <OaIdl.h>

/** @defgroup BenchtopDCServo Benchtop DC Servo
 *  This section details the Structures and Functions relavent to the  @ref BDC103_page "Benchtop DC Servo"<br />
 *  For an example of how to connect to the device and perform simple operations use the following links:
 *  <list type=bullet>
 *    <item> \ref namespaces_bdc_ex_1 "Example of using the Thorlabs.MotionControl.Benchtop.DCServo.DLL from a C or C++ project."<br />
 *									  This requires the DLL to be dynamical linked. </item>
 *    <item> \ref namespaces_bdc_ex_2 "Example of using the Thorlabs.MotionControl.Benchtop.DCServo.DLL from a C# project"<br />
 *									  This uses Marshalling to load and access the C DLL. </item>
 *  </list>
 *  The Thorlabs.MotionControl.Benchtop.DCServo.DLL requires the following DLLs
 *  <list type=bullet>
 *    <item> Thorlabs.MotionControl.DeviceManager. </item>
 *  </list>
 *  @{
 */

extern "C"
{
/// \cond NOT_MASTER

	/// <summary> Values that represent FT_Status. </summary>
	typedef enum FT_Status : short
	{
		FT_OK = 0x00, /// <OK - no error.
		FT_InvalidHandle = 0x01, ///<Invalid handle.
		FT_DeviceNotFound = 0x02, ///<Device not found.
		FT_DeviceNotOpened = 0x03, ///<Device not opened.
		FT_IOError = 0x04, ///<I/O error.
		FT_InsufficientResources = 0x05, ///<Insufficient resources.
		FT_InvalidParameter = 0x06, ///<Invalid parameter.
		FT_DeviceNotPresent = 0x07, ///<Device not present.
		FT_IncorrectDevice = 0x08 ///<Incorrect device.
	 } FT_Status;

	/// <summary> Values that represent THORLABSDEVICE_API. </summary>
	typedef enum MOT_MotorTypes
	{
		MOT_NotMotor = 0,
		MOT_DCMotor = 1,
		MOT_DCServo = 2,
		MOT_BrushlessMotor = 3,
		MOT_CustomMotor = 100,
	} MOT_MotorTypes;

	/// <summary> Values that represent Travel Modes. </summary>
	typedef enum MOT_TravelModes : int
	{
		MOT_TravelModeUndefined,///<Undefined
		MOT_Linear = 0x01,///<Linear travel, default units are millimeters
		MOT_Rotational = 0x02,///<Rotational travel, default units are degrees
	} MOT_TravelModes;

	/// <summary> Values that represent Travel Modes. </summary>
	typedef enum MOT_TravelDirection : short
	{
		MOT_TravelDirectionUndefined,///<Undefined
		MOT_Forwards = 0x01,///<Move in a Forward direction
		MOT_Reverse = 0x02,///<Move in a Backward / Reverse direction
	} MOT_TravelDirection;

	/// <summary> Values that represent Limit Switch Directions. </summary>
	typedef enum MOT_HomeLimitSwitchDirection : short
	{
		MOT_LimitSwitchDirectionUndefined,///<Undefined
		MOT_ReverseLimitSwitch = 0x01,///<Limit switch in forward direction
		MOT_ForwardLimitSwitch = 0x04,///<Limit switch in reverse direction
	} MOT_HomeLimitSwitchDirection;

	/// <summary> Values that represent Direction Type. </summary>
	typedef enum MOT_DirectionSense : short
	{
		MOT_Normal = 0x00,///<Move / Jog direction is normal (clockwise).
		MOT_Backwards = 0x01,///<Move / Jog direction is reversed (anti clockwise).
	} MOT_DirectionSense;

	/// <summary> Values that represent the motor Jog Modes. </summary>
	typedef enum MOT_JogModes : short
	{
		MOT_JogModeUndefined = 0x00,///<Undefined
		MOT_Continuous = 0x01,///<Continuous jogging
		MOT_SingleStep = 0x02,///<Jog 1 step at a time
	} MOT_JogModes;

	/// <summary> Values that represent the motor Jog Modes. </summary>
	typedef enum MOT_StopModes : short
	{
		MOT_StopModeUndefined = 0x00,///<Undefined
		MOT_Immediate = 0x01,///<Stops immediate
		MOT_Profiled = 0x02,///<Stops using a velocity profile
	} MOT_StopModes;

	/// <summary> Values that represent the motor Button Modes. </summary>
	typedef enum MOT_ButtonModes : WORD
	{
		MOT_ButtonModeUndefined = 0x00,///<Undefined
		MOT_JogMode = 0x01,///<Jog motor in correct direction for button
		MOT_Preset = 0x02,///<Move to preset position
	} MOT_ButtonModes;

	/// <summary> Value that represent action to be taken when motor hits a limit switch. </summary>
	typedef enum MOT_LimitSwitchModes : WORD
	{
		MOT_LimitSwitchModeUndefined = 0x00,///<Undefined
		MOT_LimitSwitchIgnoreSwitch=0x01,///<Ignore limit switch
		MOT_LimitSwitchMakeOnContact=0x02,///<Switch makes on contact
		MOT_LimitSwitchBreakOnContact=0x03,///<Switch breaks on contact
		MOT_LimitSwitchMakeOnHome=0x04,///<Switch makes on contact when homing
		MOT_LimitSwitchBreakOnHome=0x05,///<Switch breaks on contact when homing
		MOT_PMD_Reserved=0x06,///<Reserved for PMD brushless servo controllers
		MOT_LimitSwitchIgnoreSwitchSwapped = 0x81,///<Ignore limit switch (swapped)
		MOT_LimitSwitchMakeOnContactSwapped = 0x82,///<Switch makes on contact (swapped)
		MOT_LimitSwitchBreakOnContactSwapped = 0x83,///<Switch breaks on contact (swapped)
		MOT_LimitSwitchMakeOnHomeSwapped = 0x84,///<Switch makes on contact when homing (swapped)
		MOT_LimitSwitchBreakOnHomeSwapped = 0x85,///<Switch breaks on contact when homing (swapped)
	} MOT_LimitSwitchModes;

	/// <summary> Value that represent action to be taken when motor hits a limit switch. </summary>
	typedef enum MOT_LimitSwitchSWModes : WORD
	{
		MOT_LimitSwitchSWModeUndefined = 0x00,///<Undefined
		MOT_LimitSwitchIgnored=0x01,///<Ignore limit switch
		MOT_LimitSwitchStopImmediate=0x02,///<Stop immediately when hitting limit switch
		MOT_LimitSwitchStopProfiled=0x03,///<Stop profiled when hitting limit switch
		MOT_LimitSwitchIgnored_Rotational=0x81,///<Ignore limit switch (rotational stage)
		MOT_LimitSwitchStopImmediate_Rotational=0x82,///<Stop immediately when hitting limit switch (rotational stage)
		MOT_LimitSwitchStopProfiled_Rotational=0x83,///<Stop profiled when hitting limit switch (rotational stage)
	} MOT_LimitSwitchSWModes;

	/// <summary> Values that represent MOT_LimitsSoftwareApproachPolicy. </summary>
	typedef enum MOT_LimitsSoftwareApproachPolicy : __int16
	{
		DisallowIllegalMoves = 0,///<Disable any move outside of the current travel range of the stage
		AllowPartialMoves,///<Truncate moves to within the current travel range of the stage.
		AllowAllMoves,///<Allow all moves, regardless of whether they are within the current travel range of the stage.
	} MOT_LimitsSoftwareApproachPolicy;

	/// <summary> Values that represent the Encoder PID Loop modes. </summary>
	typedef enum MOT_PID_LoopMode : WORD
	{
		MOT_PIDLoopModeDisabled = 0x00,///<Disabled or Undefined
		MOT_PIDOpenLoopMode = 0x01,///<Encoder is in open loop mode
		MOT_PIDClosedLoopMode = 0x02,///<Encoder is in closed loop mode
	} MOT_PID_LoopMode;

	/// <summary> Values that represent DeviceMessageClass message types. </summary>
	typedef enum MOT_MovementModes
	{
		LinearRange = 0x00,///< Fixed Angular Range defined by MinPosition and MaxPosition
		RotationalUnlimited = 0x01,///< Unlimited angle
		RotationalWrapping = 0x02,///< Angular Range 0 to 360 with wrap around
	} MOT_MovementModes;

	/// <summary> Values that represent DeviceMessageClass message types. </summary>
	typedef enum MOT_MovementDirections
	{
		Quickest = 0x00,///< Uses the shortest travel between two angles
		Forwards = 0x01,///< Only rotate in a forward direction
		Reverse = 0x02,///< Only rotate in a backward direction
	} MOT_MovementDirections;
/// \endcond

	/// <summary> Information about the device generated from serial number. </summary>
	#pragma pack(1)
	typedef struct TLI_DeviceInfo
	{
		/// <summary> The device Type ID, see \ref C_DEVICEID_page "Device serial numbers". </summary>
		DWORD typeID;
		/// <summary> The device description. </summary>
		char description[65];
		/// <summary> The device serial number. </summary>
		char serialNo[16];
		/// <summary> The USB PID number. </summary>
		DWORD PID;

		/// <summary> <c>true</c> if this object is a type known to the Motion Control software. </summary>
		bool isKnownType;
		/// <summary> The motor type (if a motor).
		/// 		  <list type=table>
		///				<item><term>MOT_NotMotor</term><term>0</term></item>
		///				<item><term>MOT_DCMotor</term><term>1</term></item>
		///				<item><term>MOT_DCServo</term><term>2</term></item>
		///				<item><term>MOT_BrushlessMotor</term><term>3</term></item>
		///				<item><term>MOT_CustomMotor</term><term>100</term></item>
		/// 		  </list> </summary>
		MOT_MotorTypes motorType;

		/// <summary> <c>true</c> if the device is a piezo device. </summary>
		bool isPiezoDevice;
		/// <summary> <c>true</c> if the device is a laser. </summary>
		bool isLaser;
		/// <summary> <c>true</c> if the device is a custom type. </summary>
		bool isCustomType;
		/// <summary> <c>true</c> if the device is a rack. </summary>
		bool isRack;
		/// <summary> Defines the number of channels available in this device. </summary>
		short maxChannels;
	} TLI_DeviceInfo;

	/// <summary> Structure containing the Hardware Information. </summary>
	typedef struct TLI_HardwareInformation
	{
		/// <summary> The device serial number. </summary>
		/// <remarks> The device serial number is a serial number,<br />starting with 2 digits representing the device type<br /> and a 6 digit unique value.</remarks>
		DWORD serialNumber;
		/// <summary> The device model number. </summary>
		/// <remarks> The model number uniquely identifies the device type as a string. </remarks>
		char modelNumber[8];
		/// <summary> The device type. </summary>
		/// <remarks> Each device type has a unique Type ID: see \ref C_DEVICEID_page "Device serial numbers" </remarks>
		WORD type;
		/// <summary> The device firmware version. </summary>
		DWORD firmwareVersion;
		/// <summary> The device notes read from the device. </summary>
		char notes[48];
		/// <summary> The device dependant data. </summary>
		BYTE deviceDependantData[12];
		/// <summary> The device hardware version. </summary>
		WORD hardwareVersion;
		/// <summary> The device modification state. </summary>
		WORD modificationState;
		/// <summary> The number of channels the device provides. </summary>
		short numChannels;
	} TLI_HardwareInformation;

	/// <summary> Structure containing the velocity parameters. </summary>
	/// <remarks> Moves are performed using a velocity profile.<br />
	/// 		  The move starts at the Minimum Velocity (always 0 at present) and accelerated to the Maximum Velocity using the defined Acceleration.<br/>
	/// 		  The move is usually completed using a similar deceleration.<br/>
	/// 		  For further information see \ref C_MOTOR_sec11 "Positioning" </remarks>
	/// <seealso cref="MOT_JogParameters"/>
	/// <seealso cref="MOT_HomingParameters"/>
	typedef struct MOT_VelocityParameters
	{
		/// <summary> The minimum velocity in \ref DeviceUnits_page usually 0. </summary>
		int minVelocity;
		/// <summary> The acceleration in \ref DeviceUnits_page. </summary>
		int acceleration;
		/// <summary> The maximum velocity in \ref DeviceUnits_page. </summary>
		int maxVelocity;
	} MOT_VelocityParameters;
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

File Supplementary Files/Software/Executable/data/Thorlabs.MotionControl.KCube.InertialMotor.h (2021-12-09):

// summary:	Declares the functions class
// The following ifdef block is the standard way of creating macros which make exporting 
// from a DLL simpler. All files within this DLL are compiled with the TCUBEInertialMotor_EXPORTS
// symbol defined on the command line. This symbol should not be defined on any project
// that uses this DLL. This way any other project whose source files include this file see 
// KCUBEINERTIALMOTOR_API functions as being imported from a DLL, whereas this DLL sees symbols
// defined with this macro as being exported.
#ifdef KCUBEINERTIALMOTORDLL_EXPORTS
#define KCUBEINERTIALMOTOR_API __declspec(dllexport)
#else
#define KCUBEINERTIALMOTOR_API __declspec(dllimport)
#endif

#include <OaIdl.h>

#pragma once

/** @defgroup KCubeInertialMotor KCube InertialMotor
 *  This section details the Structures and Functions relavent to the  @ref KIM101_page "InertialMotor"<br />
 *  For an example of how to connect to the device and perform simple operations use the following links:
 *  <list type=bullet>
 *    <item> \ref namespaces_kim_ex_1 "Example of using the Thorlabs.MotionControl.KCube.InertialMotor.DLL from a C or C++ project."<br />
 *									  This requires the DLL to be dynamical linked. </item>
 *    <item> \ref namespaces_kim_ex_2 "Example of using the Thorlabs.MotionControl.KCube.InertialMotor.DLL from a C# project"<br />
 *									  This uses Marshalling to load and access the C DLL. </item>
 *  </list>
 *  The Thorlabs.MotionControl.KCube.InertialMotor.DLL requires the following DLLs
 *  <list type=bullet>
 *    <item> Thorlabs.MotionControl.DeviceManager. </item>
 *  </list>
 *  @{
 */
extern "C"
{
	/// \cond NOT_MASTER

		/// <summary> Values that represent FT_Status. </summary>
	typedef enum FT_Status : short
	{
		FT_OK = 0x00, /// <OK - no error.
		FT_InvalidHandle = 0x01, ///<Invalid handle.
		FT_DeviceNotFound = 0x02, ///<Device not found.
		FT_DeviceNotOpened = 0x03, ///<Device not opened.
		FT_IOError = 0x04, ///<I/O error.
		FT_InsufficientResources = 0x05, ///<Insufficient resources.
		FT_InvalidParameter = 0x06, ///<Invalid parameter.
		FT_DeviceNotPresent = 0x07, ///<Device not present.
		FT_IncorrectDevice = 0x08 ///<Incorrect device.
	} FT_Status;

	/// <summary> Values that represent THORLABSDEVICE_API. </summary>
	typedef enum MOT_MotorTypes
	{
		MOT_NotMotor = 0,
		MOT_DCMotor = 1,
		MOT_StepperMotor = 2,
		MOT_BrushlessMotor = 3,
		MOT_CustomMotor = 100,
	} MOT_MotorTypes;
	/// \endcond
#pragma pack(1)

	/// <summary> Values that represent kim stages. </summary>
	typedef enum KIM_Stages : unsigned short
	{
		/// <summary> An enum constant representing the undefined stage option. </summary>
		Undefined_stage = 0,
		/// <summary> An enum constant representing the PIA stage option. </summary>
		PIA_stage = 1,
		/// <summary> An enum constant representing the PD(R) stage option. </summary>
		PDR_Stage = 2,
	} KIM_Stages;

	/// <summary> Values that represent KIM_Channels. </summary>
	typedef enum KIM_Channels : unsigned __int16
	{
		/// <summary> An enum constant representing the channel 1 option. </summary>
		Channel1 = 1,
		/// <summary> An enum constant representing the channel 2 option. </summary>
		Channel2,
		/// <summary> An enum constant representing the channel 3 option. </summary>
		Channel3,
		/// <summary> An enum constant representing the channel 4 option. </summary>
		Channel4
	} KIM_Channels;
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

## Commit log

2021-10-13 update 4
    [CAD_File 1.step, CAD_File 10.step, CAD_File 11.step, CAD_File 12.step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]
2021-12-09 Software upload
    [Configuration.csv, sequence.csv]
2021-12-09 Update List of Items.xlsx
    [List of Items.xlsx]
